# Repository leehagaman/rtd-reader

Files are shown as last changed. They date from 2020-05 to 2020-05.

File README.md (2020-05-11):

# 16 Channel PT1000 Reader

This project describes an Arduino shield which allows the reading of up to 16 PT1000 2 wire RTD temperature sensors, and communicate that information to a computer. It also has two digital outputs, designed to control relays which can turn heaters on and off. This design allows the Arduino to autonomously control the heaters, ensuring consistent temperature control even if the main computer loses connection.

<p align="center">
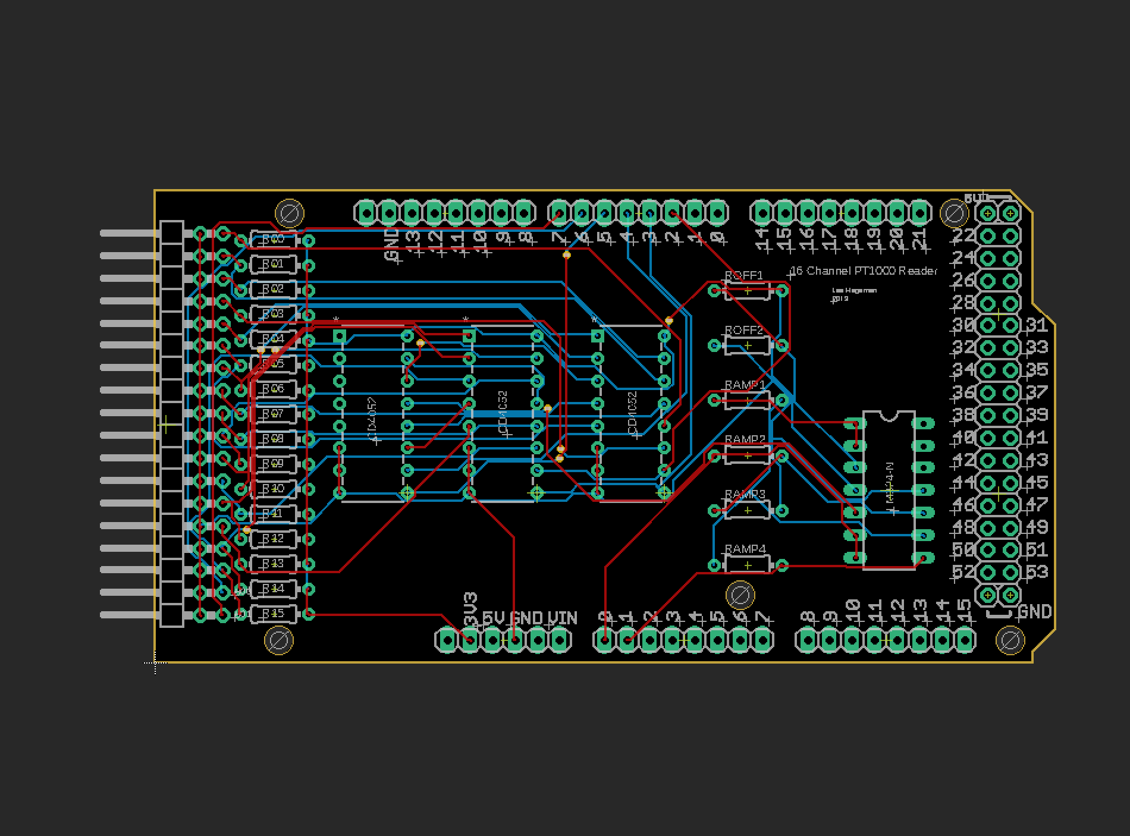
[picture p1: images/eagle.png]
  
</p>

## Getting Started

### Materials

To make the Arduino shield, you need the following items:

- 1 Arduino Due or Arduino Mega (with corresponding cable, and power supply if you'd like continued operation in the event of a computer failure)
- 1 Printed Circuit Board (see .brd file)
- 1 LM324 Op Amp chip [link](https://www.digikey.com/product-detail/en/texas-instruments/LM324N/296-1391-5-ND/277627)
- 3 CD4052B Multiplexing chips [link](https://www.digikey.com/product-detail/en/texas-instruments/CD4051BE/296-2057-5-ND/67305)
- 18 0.1" double right angle connectors [link](https://www.digikey.com/products/en?mpart=PREC040SFAN-RC&v=35)
- 40 0.1" straight connectors [link](https://www.digikey.com/products/en?mpart=PREC040SFAN-RC&v=35)
- 16 1kΩ resistors
- 6 amplification resistors (optional, see "choosing resistors" section)

### Choosing Resistors

For the 16 1kΩ resistors, you can measure and record their specific resistances after installation for increased accuracy, so there is no special process to choose them.

The Arduino will constantly measure an unamplified temperature, which has a resolution which varies from about 0.1°C near -200°C, to about 1°C near 40°C (this is calculated using 10 bit resolution, an Arduino Due can be configured to use 12 bits instead, giving 100 times finer resolution). 

<p align="center">
  
</p>

<p align="center">Serial monitor output comparing amplified and unamplified measurements. These curves were obtained by pinching a PT1000 with my fingers and then releasing. The overall offset can likely be fixed with calibration. (Image will be updated to a cleaner one soon.)</p>

To improve this resolution, the Arduino will also measure an amplified temperature, which lets you effectively "zoom in" on an specific temperature range (see above comparison). There is a several step process to determine the ideal resistors for a given temperature range of interest.

1. Decide on T<sub>min</sub> and T<sub>max</sub>, the minimum and maximum temperatures you plan to measure with your amplified circuit.
2. Calculate the R<sub>min</sub> and R<sub>max</sub>, the corresponding minimum and maximum PT1000 resistances (use something like [this table](https://web.mst.edu/~cottrell/ME240/Resources/Temperature/RTD%20table.pdf))
3. Calculate V<sub>min</sub> and V<sub>max</sub>, the corresponding voltages read by the Arduino. Use the formula V=R/(R+1000Ω)*(3.3 Volts).
4. We have our unamplified voltage range, and we will use our amplifier to convert this to our desired voltage range of 0.1V-1.7V (the op-amp only gets within 1.5V of the maximum, so the measurable range is 0-1.8V, and we give each side 0.1V of buffer). So, the desired amplification factor is A=(V<sub>max</sub>- V<sub>min</sub>)/(1.6 Volts). We also have an ideal offset voltage V<sub>off</sub>  equal to V<sub>min</sub>.
5. Now that we have ideal A and V<sub>off</sub> values chosen, we must modify them to make their values easy to construct with available resistors. We must choose resistors with resistance values R<sub>1</sub>, R<sub>2</sub>, R<sub>off1</sub>, and R<sub>off2</sub> such that A=R<sub>2</sub>/R<sub>1</sub> and  V<sub>off</sub>=V<sub>min</sub>. It is perfectly fine to decrease A and adjust V<sub>off</sub> in order to accomplish this without having to use nonstandard resistors, it will just slightly change the range of voltages, which is why we gave each side 0.1V of buffer in step 4. 
6. To check that your resistance values will work as expected, recalculate your amplified voltage range. The amplified voltage will be V<sub>amp </sub>= R<sub>2</sub>/R<sub>1</sub> * (V - (3.3 Volts) * R<sub>off2</sub> / (R<sub>off1</sub> + R<sub>off2</sub> )) where V is the unamplified voltage. It's a good idea to use that formula to double check that the amplified voltage will stay in the range 0 to 1.7 Volts for the expected unamplified voltages from step 3.

Now that we have our desired resistor values, R<sub>1</sub>, R<sub>2</sub>, R<sub>off1</sub>, and R<sub>off2</sub>, we need to choose resistors with those resistance values. We need a pair of resistors, R<sub>amp1</sub> and R<sub>amp2</sub>, to have resistances as close as possible to R<sub>1</sub>, and another pair R<sub>amp3</sub> and R<sub>amp4</sub>, to have resistances as close as possible to R<sub>amp1</sub> and R<sub>2</sub>. It is worth taking some time to match the resistances of each pair, as the linearity of the amplifier depends on their values being equal. Once you have also chosen R<sub>off1</sub> and R<sub>off2</sub>, take the time to measure and record the resistances of each resistor, as their precise values are used by the arduino program to reconstruct the temperature from the amplified voltage, and the resistances cannot be simply measured after soldering.

### Assembly

Soldering can be done in any order, but I recommend soldering the pin connectors last as they can give you less room to solder the 16 1kΩ resistors.

### Program Modification

In the Arduino file, you should modify the parameters to correspond to your measured resistances and active channels. You can also switch between LabVIEW output and serial monitor output.

I plan to improve the readability of the arduino code once the LabVIEW integration is finalized.

### Calibration

Will be updated soon. I should be able to use a known temperature to calibrate the temperature measurements, as well as matching the amplified measurement to the unamplified measurement just using the ambient room temperature.

## LabVIEW Integration

Will be updated soon. I plan to support output of temperature as well as input of desired temperature windows.

## Acknowledgments

* Domenico Franco helped me iterate the PCB design.

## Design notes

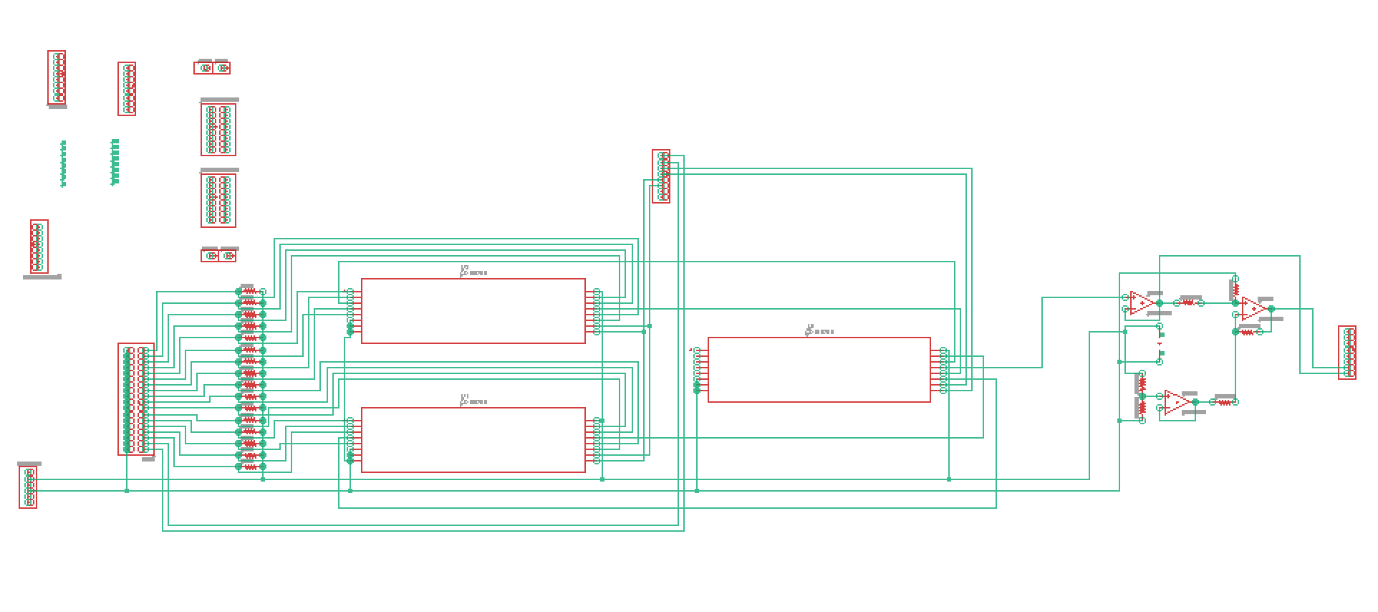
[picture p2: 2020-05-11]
images/diagram.png

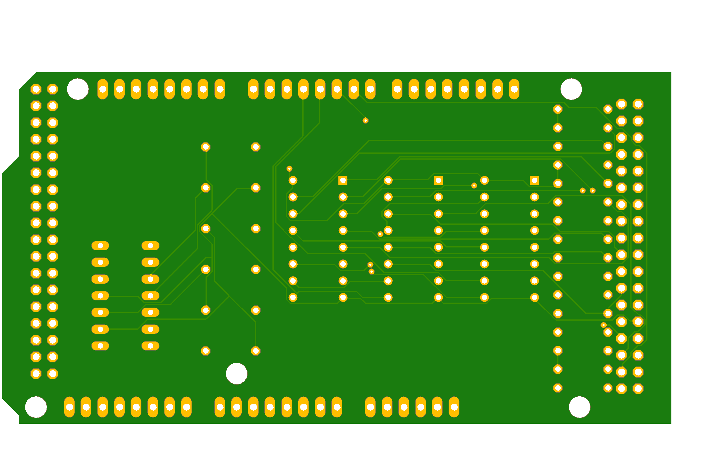
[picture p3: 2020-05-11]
images/pcb_back.png

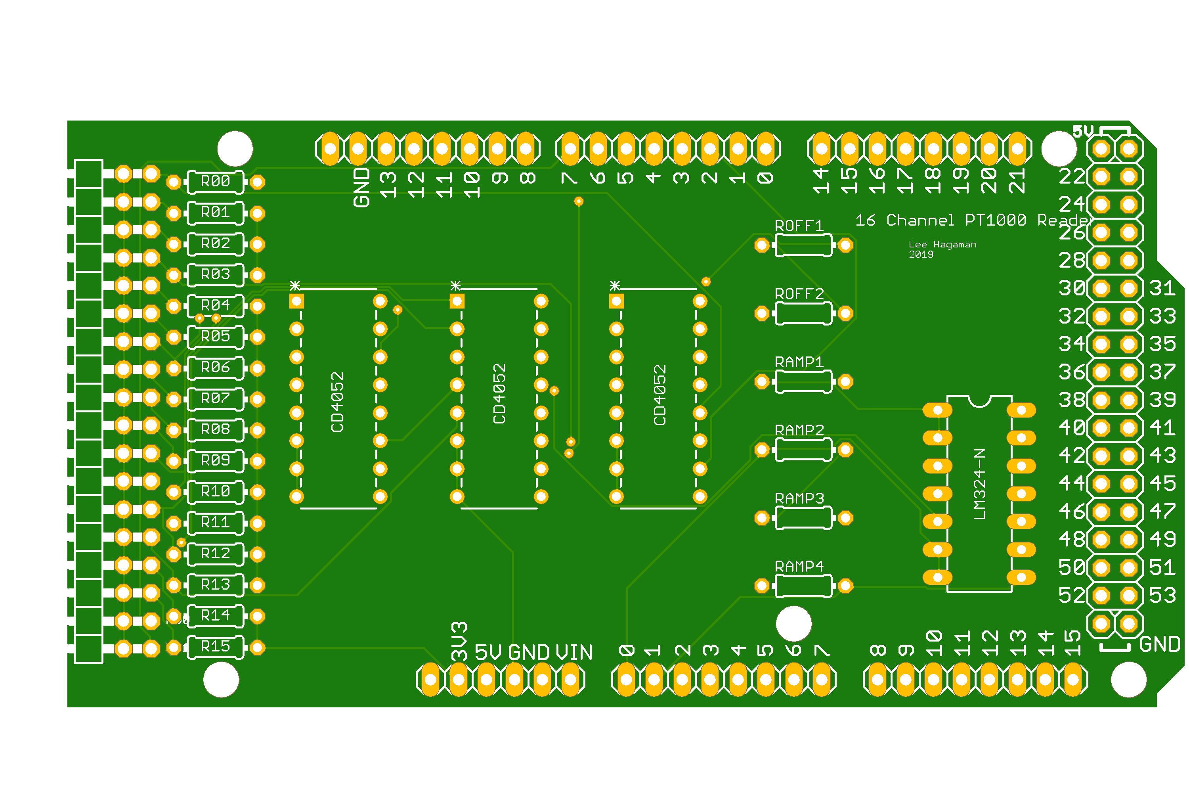
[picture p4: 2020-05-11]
images/pcb.png

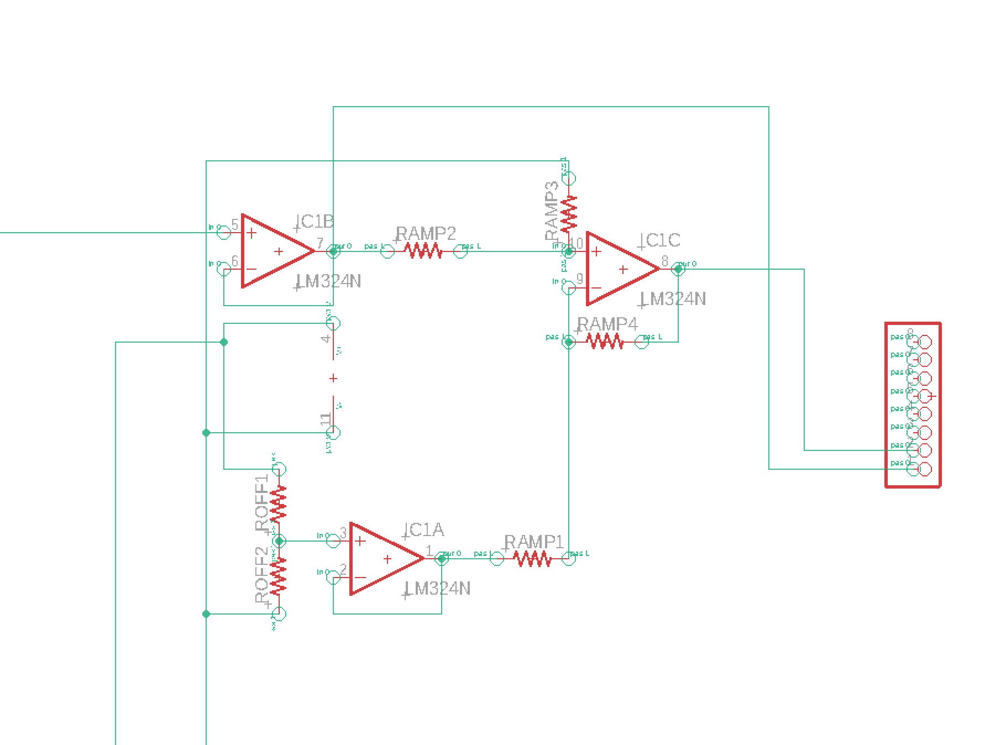
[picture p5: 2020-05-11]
images/diagram_amp_zoom.png

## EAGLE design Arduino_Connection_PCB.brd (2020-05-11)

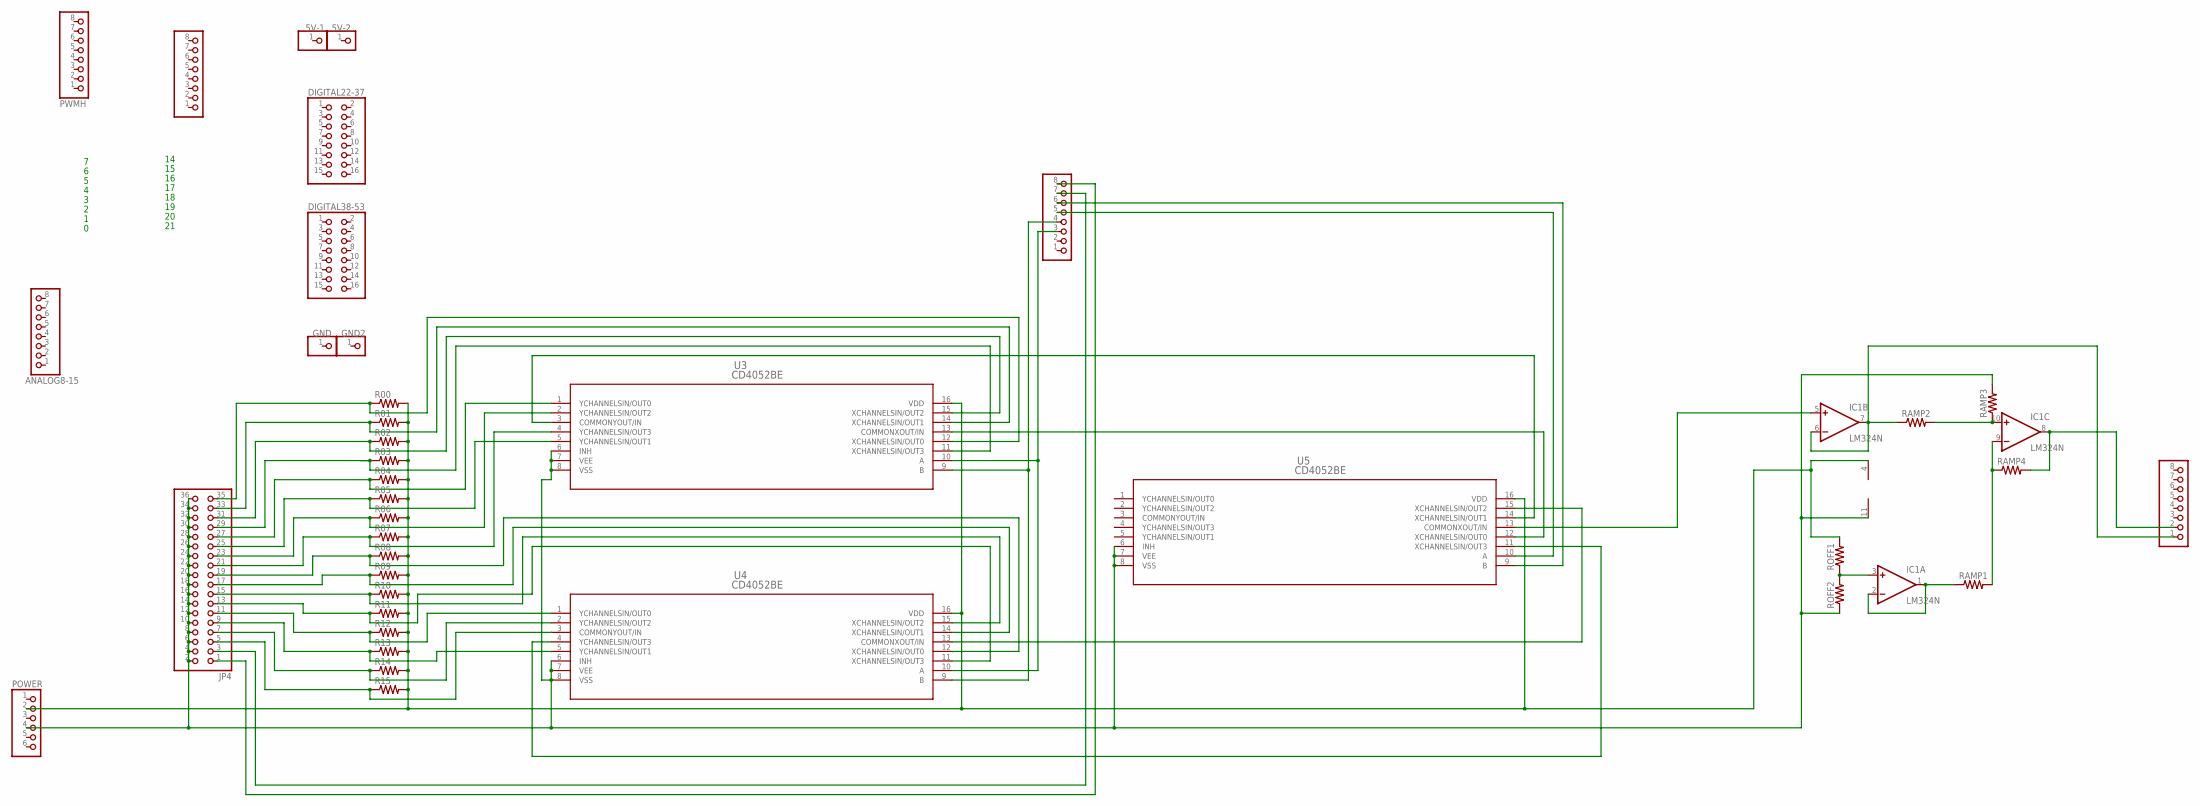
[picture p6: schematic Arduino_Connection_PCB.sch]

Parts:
5V-1, 5V-2: PINHD-1X1; 1X01
ANALOG0-7, ANALOG8-15: PINHD-1X8; 1X08
COMMUNICATION: PINHD-1X8; 1X08
DIGITAL22-37, DIGITAL38-53: PINHD-2X8; 2X08
GND, GND2: PINHD-1X1; 1X01
IC1: LM324N; DIL14
JP4: PINHD-2X18/90; 2X18/90
POWER: PINHD-1X6; 1X06
PWMH: PINHD-1X8; 1X08
PWML: PINHD-1X8; 1X08
R00, R01, R02, R03, R04, R05, R06, R07, R08, R09, R10, R11, R12, R13, R14, R15: R-US_0204/7; 0204/7
RAMP1, RAMP2, RAMP3, RAMP4: R-US_0204/7; 0204/7
ROFF1, ROFF2: R-US_0204/7; 0204/7
U3, U4, U5: CD4052BE; N16

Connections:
unnamed: IC1.5 (+IN), U5.13 (COMMONXOUT/IN)
unnamed: ANALOG0-7.1, IC1.6 (-IN), IC1.7 (OUT), RAMP2.1
unnamed: JP4.3, PWML.7
unnamed: JP4.1, PWML.8
unnamed: IC1.3 (+IN), ROFF1.1, ROFF2.2
unnamed: IC1.11 (V-), JP4.2, JP4.4, JP4.6, JP4.8, JP4.10, JP4.12, JP4.14, JP4.16, JP4.18, JP4.20, JP4.22, JP4.24, JP4.26, JP4.28, JP4.30, JP4.32, JP4.34, JP4.36, POWER.4, RAMP3.2, ROFF2.1, U3.6 (INH), U3.7 (VEE), U3.8 (VSS), U4.6 (INH), U4.7 (VEE), U4.8 (VSS), U5.6 (INH), U5.7 (VEE), U5.8 (VSS)
unnamed: JP4.13, R11.1, U4.11 (XCHANNELSIN/OUT3)
unnamed: PWML.3, U3.10 (A), U4.10 (A)
unnamed: IC1.4 (V+), POWER.2, R00.2, R01.2, R02.2, R03.2, R04.2, R05.2, R06.2, R07.2, R08.2, R09.2, R10.2, R11.2, R12.2, R13.2, R14.2, R15.2, ROFF1.2, U3.16 (VDD), U4.16 (VDD), U5.16 (VDD)
unnamed: JP4.25, R05.1, U3.5 (YCHANNELSIN/OUT1)
unnamed: JP4.35, R00.1, U3.12 (XCHANNELSIN/OUT0)
unnamed: PWML.4, U3.9 (B), U4.9 (B)
unnamed: JP4.19, R08.1, U4.12 (XCHANNELSIN/OUT0)
unnamed: JP4.21, R07.1, U3.4 (YCHANNELSIN/OUT3)
unnamed: JP4.17, R09.1, U4.14 (XCHANNELSIN/OUT1)
unnamed: JP4.5, R15.1, U4.3 (COMMONYOUT/IN)
unnamed: JP4.7, R14.1, U4.2 (YCHANNELSIN/OUT2)
unnamed: JP4.9, R13.1, U4.5 (YCHANNELSIN/OUT1)
unnamed: JP4.11, R12.1, U4.1 (YCHANNELSIN/OUT0)
unnamed: PWML.5, U5.10 (A)
unnamed: JP4.15, R10.1, U4.15 (XCHANNELSIN/OUT2)
unnamed: PWML.6, U5.9 (B)
unnamed: IC1.1 (OUT), IC1.2 (-IN), RAMP1.1
unnamed: IC1.9 (-IN), RAMP1.2, RAMP4.1
unnamed: IC1.10 (+IN), RAMP2.2, RAMP3.1
unnamed: ANALOG0-7.2, IC1.8 (OUT), RAMP4.2
unnamed: U3.13 (COMMONXOUT/IN), U5.12 (XCHANNELSIN/OUT0)
unnamed: U3.3 (COMMONYOUT/IN), U5.14 (XCHANNELSIN/OUT1)
unnamed: U4.13 (COMMONXOUT/IN), U5.15 (XCHANNELSIN/OUT2)
unnamed: U4.4 (YCHANNELSIN/OUT3), U5.11 (XCHANNELSIN/OUT3)
unnamed: JP4.31, R02.1, U3.15 (XCHANNELSIN/OUT2)
unnamed: JP4.27, R04.1, U3.1 (YCHANNELSIN/OUT0)
unnamed: JP4.23, R06.1, U3.2 (YCHANNELSIN/OUT2)
unnamed: JP4.29, R03.1, U3.11 (XCHANNELSIN/OUT3)
unnamed: JP4.33, R01.1, U3.14 (XCHANNELSIN/OUT1)

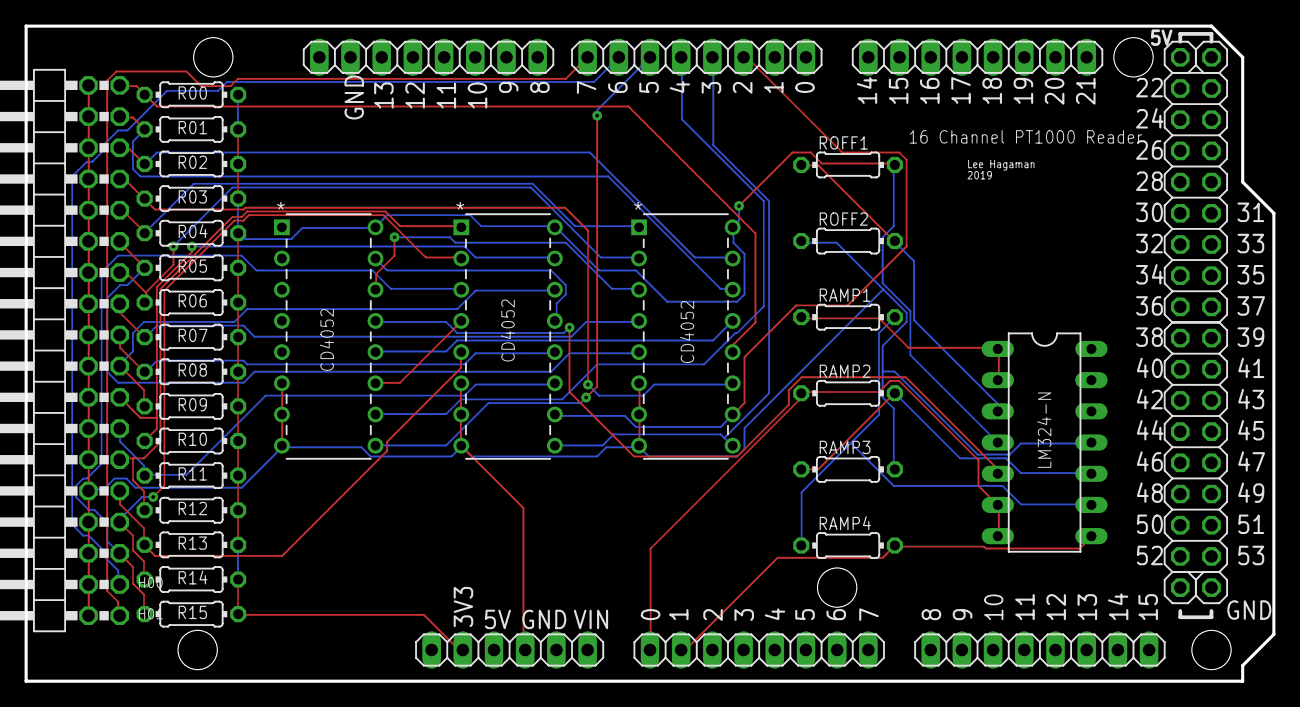
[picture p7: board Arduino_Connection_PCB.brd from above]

Board: 2 copper layers, 101.6 x 53.3 mm, 39 parts (0 on the bottom side), 35 nets.

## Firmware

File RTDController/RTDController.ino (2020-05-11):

// 16 Channel PT1000 Reader
// Lee Hagaman 2020

const int analog_pin = A0;
const int analog_pin_amp = A1;
const int heater_1_pin = 6;
const int heater_2_pin = 7;
const int digital_pin_0 = 2;
const int digital_pin_1 = 3;
const int digital_pin_2 = 4;
const int digital_pin_3 = 5;

const int resolution = pow(2,10); // 10 bit DAC
const float vmax = 3.3;
const float analog_to_voltage = vmax / resolution;

int activePTs[] = {8, 9};

// list of more precisely measured values for the 16 installed 1kOhm resistors
float resistors[] = {998.4, 983.3, 983.3, 985.0, 982.2, 985.1, 979.4, 986.5, 986.1, 983.3, 983.2, 983.0, 984.5, 982.6, 989.9, 980.7};

float roff1 = 978.7; // resistance for offset generator connected to vmax
float roff2 = 980.8; // resistance for offset generator connected to ground
float r1 = 981.8;  // resistance for amplifier, average of the measured values 982.4 and 981.2, the measured values for r1amp and r2amp
float r2 = 9735;  // resistance for amplifier, average of the measured values 9729 and 9724, the measured values for r3amp and r4amp

const int delay_after_multiplexing = 10; // milliseconds
const int delay_between_readings = 10; // milliseconds

const int numPTs = sizeof(activePTs) / sizeof(activePTs[0]);
int ptindex = 0;
int ptnum;
float v;
float v_amp;
float v_amp_converted;
float rpt;
float rpt_amp;
float temp;
float temp_amp;

// 10 * PT1000 resistance, or 100 * PT100 resistance
// -200 C to 50 C in one degree increments
// from https://github.com/drhaney/pt100rtd/blob/master/pt100rtd.h
int resistances[] = {
  1852, 1896, 1939, 1982, 2025, 2068, 2111, 2154, 2197, 2240, // -200 C
  2283, 2326, 2369, 2412, 2455, 2497, 2539, 2582, 2625, 2667, 
  2710, 2752, 2795, 2837, 2880, 2922, 2965, 3007, 3049, 3092, 
  3134, 3176, 3218, 3261, 3303, 3345, 3386, 3428, 3470, 3512, 
  3554, 3596, 3638, 3680, 3722, 3763, 3805, 3847, 3889, 3931, 
  3972, 4014, 4056, 4097, 4139, 4180, 4222, 4264, 4305, 4346, // -150 C
  4388, 4429, 4471, 4512, 4553, 4595, 4635, 4676, 4718, 4759, 
  4800, 4841, 4882, 4923, 4964, 5006, 5047, 5088, 5129, 5170, 
  5211, 5252, 5292, 5333, 5374, 5415, 5456, 5497, 5538, 5578, 
  5619, 5660, 5700, 5741, 5782, 5822, 5863, 5904, 5944, 5985, 
  6026, 6067, 6107, 6148, 6187, 6229, 6269, 6310, 6350, 6391, // -100 C
  6430, 6470, 6511, 6551, 6591, 6631, 6672, 6712, 6752, 6792, 
  6833, 6873, 6913, 6953, 6993, 7033, 7073, 7113, 7153, 7193, 
  7233, 7273, 7313, 7353, 7393, 7433, 7473, 7513, 7553, 7593,
  7633, 7673, 7713, 7752, 7792, 7832, 7872, 7911, 7951, 7991, 
  8031, 8070, 8110, 8150, 8189, 8229, 8269, 8308, 8348, 8388, //  -50 C
  8427, 8467, 8506, 8546, 8585, 8625, 8664, 8704, 8743, 8783, 
  8822, 8862, 8901, 8940, 8980, 9019, 9059, 9098, 9137, 9177,
  9216, 9255, 9295, 9334, 9373, 9412, 9452, 9491, 9530, 9569, 
  9609, 9648, 9687, 9726, 9765, 9804, 9844, 9883, 9922, 9961, 
  10000,10039,10078,10117,10156,10195,10234,10273,10312,10351, //  00 C
  10390,10429,10468,10507,10546,10585,10624,10663,10702,10740,
  10779,10818,10857,10896,10935,10973,11012,11051,11090,11128,
  11167,11206,11245,11283,11322,11361,11399,11438,11477,11515, 
  11554,11593,11631,11670,11708,11747,11785,11824,11862,11901, 
  11940};                                                      //  50 C

const int size = 251;

float gettemp(float rpt) {
  const float d = 10.0; // 10 for PT1000, 100 for PT100

  if (rpt < resistances[0] / d) return -199.99;
  if (rpt > resistances[size - 1] / d) return 49.99;
  
  int pos = 0;
  while (rpt > resistances[pos] / d) pos++;
  
  if (rpt == resistances[pos]) return pos - 200; // rare equality

  float r1 = resistances[pos-1] / d; // low value for resistance in table
  float r2 = resistances[pos] / d;   // high value for resistance in table
  int t1 = pos-1 - 200;              // low value for temperature in table
  int t2 = pos - 200;                // high value for temperature in table

  return t1 + (rpt - r1) / (r2-r1) * (t2-t1);
}

void setup() {
  Serial.begin(9600);

  Serial.println(numPTs);

  pinMode(digital_pin_0, OUTPUT);
  pinMode(digital_pin_1, OUTPUT);
  pinMode(digital_pin_2, OUTPUT);
  pinMode(digital_pin_3, OUTPUT);

  pinMode(heater_1_pin, OUTPUT);
  pinMode(heater_2_pin, OUTPUT);
}

void loop() {

  ptnum = activePTs[ptindex];
  
  digitalWrite(digital_pin_0, ptnum % 2);
  digitalWrite(digital_pin_1, (ptnum / 2) % 2);
  digitalWrite(digital_pin_2, (ptnum / 4) % 2);
  digitalWrite(digital_pin_3, (ptnum / 8) % 2);

  delay(delay_after_multiplexing);

  v = analogRead(analog_pin) * analog_to_voltage;
  v_amp = analogRead(analog_pin_amp) * analog_to_voltage;
  v_amp_converted = r1 / r2 * v_amp + vmax * roff2 / (roff1 + roff2);

  rpt = resistors[ptnum] * v / (vmax - v);
  temp = gettemp(rpt);

  rpt_amp = resistors[ptnum] * v_amp_converted / (vmax - v_amp_converted);
  temp_amp = gettemp(rpt_amp);

  /*
  Serial.print(ptnum);
  Serial.print(": ");
  Serial.print(v, 4);
  Serial.print("V, ");
  Serial.print(v_amp, 4);
  Serial.print("V, ");
  Serial.print(v_amp_converted, 4);
  Serial.print("V, ");
  Serial.print(rpt_amp);
  Serial.print("Ω, ");
  Serial.print(temp_amp, 4);
  Serial.print("C, ");
  Serial.print(temp_amp * 9. / 5. + 32., 4);
  Serial.println("F");
  */
  

  // this used for arduino serial plotter
  /*
  Serial.print(ptnum);
  Serial.print(":");
  Serial.print(temp, 4);
  Serial.print("   ");
  if (ptnum == numPTs - 1) {
    Serial.println("");
  }
  */
  
  Serial.print(ptnum);
  Serial.print(":");
  Serial.print(temp, 4);
  Serial.print("    ");
  Serial.print(ptnum);
  Serial.print("_amp:");
  Serial.print(temp_amp, 4);
  Serial.print("   ");
  if (ptindex == numPTs - 1) {
    Serial.println("");
  }

  // this used for labview
  /*
  Serial.print(ptnum);
  Serial.print(": ");
  Serial.print(temp);
  Serial.println("");
  */

  if (ptindex == numPTs - 1) {
    ptindex = 0;
  } else {
    ptindex++;
  }
  
  delay(delay_between_readings);
}
